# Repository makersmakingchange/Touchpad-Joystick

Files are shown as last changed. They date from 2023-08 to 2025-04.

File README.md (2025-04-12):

<!---  Open Source Assistive Technology: GitHub Readme Template  --->
<!-- Template files available at https://github.com/makersmakingchange/OpenAT-Template -->
 
<!-- TITLE -->
# Touchpad Joystick

<!-- SUMMARY -->
The Touchpad Joystick is a joystick that is activated by touch. This device is a more affordable option to many commercial joysticks and trackpads on the market. This is a USB joystick that can be plugged into either the left, or right USB joystick of the Xbox Adaptive Controller.

The Touchpad Joystick is comprised of a commercially available capacitive touch sensor (Cirque Capacitive Touch Sensor 35 mm) that is mounted in a 3d printed enclosure.

This Joystick was designed by Ron Nelson. 

<!-- PHOTO --->
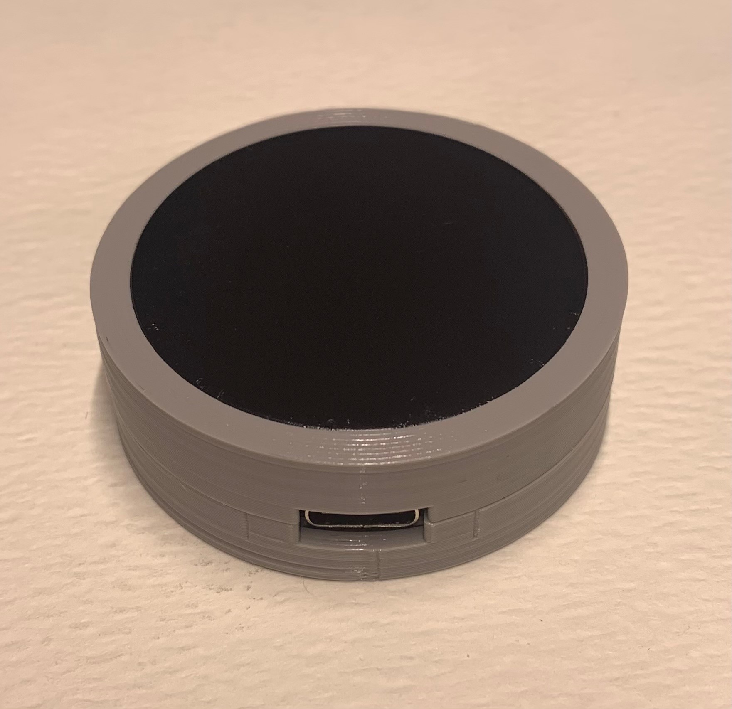
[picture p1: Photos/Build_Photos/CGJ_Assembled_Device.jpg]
Touchpad joystick with a grey case.


## Makers Making Change Assistive Device Library
 - https://www.makersmakingchange.com/s/product/touchpad-joystick/](https://www.makersmakingchange.com/s/product/touchpad-joystick/01tJR000000Be3lYAC

## Getting Started

### 1. Order the Off-The-Shelf Components
The [Bill of Materials](/Documentation/Touchpad_Joystick_BOM.csv) lists all of the parts and components required to build the Touchpad Joystick. The electronic components may be available locally, but will probably need to be ordered online. 

### 2. Print the 3D Printable components
Print the components for the switch tester case and choose an option for the case.

All of the files and individual print files can be in the [/Build_Files/3D_Printing_Files](/Build_Files/3D_Printing_Files/) folder.

### 3. Assemble the Touchpad Joystick
Reference the [assembly guide](/Documentation/Touchpad_Joystick_Assembly_Guide.pdf) for the tools and steps required to build each portion.

## Files
<!--- FILES --->

### Documentation
<!--- DOCUMENTATION --->
| Document | Version | Link |
|----------|---------|------|
| Design Rationale     | 1.0 | [Touchpad_Joystick_Design_Rationale](/Documentation/Touchpad_Joystick_Design_Rationale.pdf) |
| Bill of Materials    | 1.0 | [Touchpad_Joystick_BOM](/Documentation/Touchpad_Joystick_BOM.csv) |
| Assembly Guide       | 1.0 | [Touchpad_Joystick_Assembly_Guide](/Documentation/Touchpad_Joystick_Assembly_Guide.pdf) |
| Maker Checklist      | 1.0 | [Touchpad_Joystick_Checklist](/Documentation/Touchpad_Joystick_Maker_Checklist.pdf) |
| User Quick Guide     | 1.0 | [Touchpad_Joystick_User_Quick_Guide](/Documentation/Touchpad_Joystick_User_Guide.pdf)           |
| Changelog            | 1.0 | [Touchpad_Joystick_Changelog](/Documentation/Touchpad_Joystick_Changelog.pdf)               |

### Build Files
<!--- BUILD FILES --->
 - [3D Printing Files](/Build_Files/3D_Printing_Files)

## License
<!--- LICENSE --->
Everything needed or used to design, make, test, or prepare the Touchpad Joystick is licensed under the CERN 2.0 Weakly Reciprocal license <https://ohwr.org/project/cernohl/wikis/Documents/CERN-OHL-version-2> (CERN-OHL-W).

All software is under the GNU General Public License v3.0 (GPL-3.0). 

Accompanying material such as instruction manuals, videos, and other copyrightable works that are useful but not necessary to design, make, test, or prepare the Touchpad Joystick are published under a Creative Commons Attribution-ShareAlike 4.0 license <https://creativecommons.org/licenses/by-sa/4.0/> (CC BY-SA 4.0).

## Attribution
<!--- ATTRIBUTION --->
 - The original design was created by [Ron Nelson](https://github.com/nelsonii) under an [MIT License](https://github.com/nelsonii/JoystickEnclosures/blob/main/LICENSE)
 - Documentation by Neil Squire Society / Makers making Change
 - The documentation template was created by [Neil Squire](https://www.neilsquire.ca/) / [Makers Making Change](https://makersmakingchange.com/) and is used under a CC BY-SA 4.0 license. It is available at the following link: https://github.com/makersmakingchange/OpenAT-Template

----

<!-- ABOUT MMC START -->
## About Makers Making Change
[Makers Making Change Logo](https://www.makersmakingchange.com/)

Makers Making Change is a program of [Neil Squire](https://www.neilsquire.ca/), a Canadian non-profit that uses technology, knowledge, and passion to empower people with disabilities.

Makers Making Change leverages the capacity of community based Makers, Disability Professionals and Volunteers to develop and deliver affordable Open Source Assistive Technologies.

 - Website: [www.MakersMakingChange.com](https://www.makersmakingchange.com/)
 - GitHub: [makersmakingchange](https://github.com/makersmakingchange)
 - Bluesky: [@makersmakingchange.bsky.social](https://bsky.app/profile/makersmakingchange.bsky.social)
 - Instagram: [@makersmakingchange](https://www.instagram.com/makersmakingchange)
 - Facebook: [makersmakechange](https://www.facebook.com/makersmakechange)
 - LinkedIn: [Neil Squire Society](https://www.linkedin.com/company/neil-squire-society/)
 - Thingiverse: [makersmakingchange](https://www.thingiverse.com/makersmakingchange/about)
 - Printables: [MakersMakingChange](https://www.printables.com/@MakersMakingChange)

### Contact Us
For technical questions, to get involved, or to share your experience we encourage you to [visit our website](https://www.makersmakingchange.com/) or [contact us](https://www.makersmakingchange.com/s/contact).
<!-- ABOUT MMC END -->

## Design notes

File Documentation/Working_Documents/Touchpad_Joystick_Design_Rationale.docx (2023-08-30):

# Introduction

This device is a capacitive touchscreen joystick that allows users to connect to the XAC and operate a joystick with little to zero force. This device is well suited for users with limited dexterity and finger strength.

# Research

## Commercial Products

Title | Picture | Price | Notes

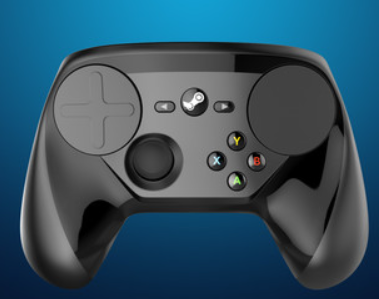
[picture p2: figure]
A photo of the Steam controller.

Steam Controller (https://store.steampowered.com/app/353370/Steam_Controller/) | | N/A | This commercial gaming controller made by Steam uses a trackpad joystick instead of the standard analog joystick. Considered a commercial flop and is no longer available.

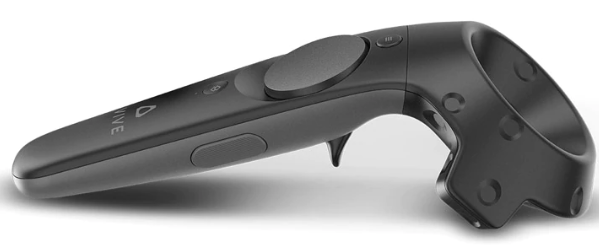
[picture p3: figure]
A photo of the Vive controller.

Vive Controller (https://www.vive.com/ca/accessory/controller/) | | $179.99 | A controller used for VR gaming that uses a track pad joystick

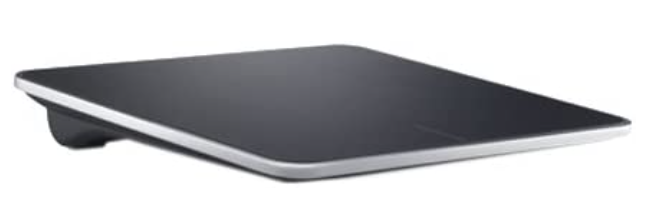
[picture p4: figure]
A photo of the Dell Wireless Touchpad.

Dell Wireless Touchpad (https://www.amazon.com/dp/B00AM0SI16/?tag=tguru-20&th=1) | | $109.99 | A wireless trackpad that can connect to a computer through a USB dongle.

## DIY Products

Title | Picture | Price | Notes

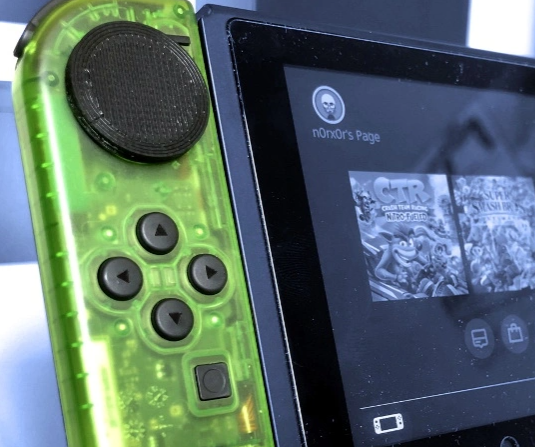
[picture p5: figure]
A photo of the Joy-Con touchpad mod.

Joy-Con Touchpad Mod (https://medium.com/@matteo.pisani.91/how-i-hacked-nintendo-joy-con-controller-8ac22d75b0b8) | | | “The initial inspiration for this project was to create a permanent solution to joystick fatigue and drifting issues” Replaces the stock joystick with the Cirque GlidePoint (https://www.cirque.com/glidepoint-circle-trackpads) capacitive joystick.

# Requirements

## Goals

G01 | Offer users an alternative to analog joysticks.
G02 | Allow users to control their joystick with little to no activation force.
G03 | Use capacitive touch to control joystick movements.

## Functional Requirements

F01 | Must be compatible with the XAC.
F02 | Must use common connection types to connect the device to the XAC.

## Non-functional Requirement

NF01 | 3D printed parts must be printable on common maker printers.
NF02 | 3D printed parts should be printable with no supports.

## Constraints

C01 | Must use readily available off the shelf parts.
C02 | Must be buildable using common maker tools.

# Version 1.0

## GlidePoint Joystick MKII

Designer: Ron Nelson

Cost: ~$32

Print Time: ~1h

GitHub Repository: nelsonii (Ron Nelson) (github.com) (https://github.com/nelsonii)

- Contains firmware and housing designs for various devices made by Ron Nelson, including the glide point joystick.

YouTube: GlidePoint as Joystick for XBOX Adaptive Controller - YouTube (https://www.youtube.com/watch?v=LsAF-lyaMcg)

- Brief explanation of the prototyping process.

Other Resources:

ATMakers - Makers & Users | Facebook (https://www.facebook.com/groups/ATMakers/) – Some discussion of device.

Cirque Glidepoint Light Touch Switch - YouTube (https://www.youtube.com/watch?v=ezXU3xq22Q4) – Review of product.

SevenMileMountain - Etsy Canada (https://www.etsy.com/shop/SevenMileMountain?) – Etsy shop where Ron Nelson currently sells mounts for this device.

### Cirque GlidePoint Sensor

The GlidePoint is a capacitive trackpad that is used as a joystick in this project. There are three sizes available: 23 mm, 35 mm, and 40 mm in diameter.

There are also 4 different top surfaces available:

1. Curved Overlay
2. Flat Overlay
3. Adhesive Overlay
4. No Overlay

### Device Configurations

Configuration | GlidePoint Variants | Microcontroller Options | Enclosure
1 (MKII) | - 35 mm - Curved Overlay (https://www.mouser.ca/ProductDetail/355-TM0350352024-003) | - QT PY SAMD21 (https://www.mouser.ca/ProductDetail/485-4600) - QT PY RP2040 (https://www.mouser.ca/ProductDetail/485-4900) | - Top (https://github.com/nelsonii/JoystickEnclosures/blob/main/CirquePoint/CirqueGlidePointMKII_Enclosure_QTPy_Top_Disc_35mmWithOverlay_v1A.stl) - Base (https://github.com/nelsonii/JoystickEnclosures/blob/main/CirquePoint/CirqueGlidePointMKII_Enclosure_QTPy_Bottom_35mmWithOverlay_v1A.stl)
2 | - 23 mm - Flat Overlay (https://www.mouser.ca/ProductDetail/Cirque/TM023023-2024-002?qs=sGAEpiMZZMu3sxpa5v1qrmePy6bg6o9mPlv2NExs3Z8%3D) - 23mm - No Overlay (https://www.mouser.ca/ProductDetail/Cirque/TM023023-2024-000?qs=sGAEpiMZZMu3sxpa5v1qrmePy6bg6o9mqjFnvRi8yK8%3D) | - QT PY SAMD21 (https://www.mouser.ca/ProductDetail/485-4600) - QT PY RP2040 (https://www.mouser.ca/ProductDetail/485-4900) | - Top (https://github.com/nelsonii/JoystickEnclosures/blob/main/CirquePoint/CirquePoint_Enclosure_QTPy_Top_Disc_23mm_QTPy_v1H.stl) - Base (https://github.com/nelsonii/JoystickEnclosures/blob/main/CirquePoint/CirquePoint_Enclosure_QTPy_Bottom_23mm_v1H.stl)
3 | - 35 mm - Flat Overlay (https://www.mouser.ca/ProductDetail/Cirque/TM035035-2024-002?qs=sGAEpiMZZMu3sxpa5v1qrmePy6bg6o9mljGtaoJl40o%3D) - 35 mm - Adhesive Overlay (https://www.mouser.ca/ProductDetail/Cirque/TM035035-2024-001) - 35 mm - No Overlay (https://www.mouser.ca/ProductDetail/Cirque/TM035035-2024-000?qs=sGAEpiMZZMu3sxpa5v1qrmePy6bg6o9mfunfVZT7bg4%3D) | - QT PY SAMD21 (https://www.mouser.ca/ProductDetail/485-4600) - QT PY RP2040 (https://www.mouser.ca/ProductDetail/485-4900) | - Top (https://github.com/nelsonii/JoystickEnclosures/blob/main/CirquePoint/CirquePoint_Enclosure_QTPy_Top_Disc_35mm_QTPy_v1H.stl) - Base (https://github.com/nelsonii/JoystickEnclosures/blob/main/CirquePoint/CirquePoint_Enclosure_QTPy_Bottom_35mm_v1H.stl)
4 | - 40 mm - Flat Overlay (https://www.mouser.ca/ProductDetail/Cirque/TM040040-2024-302) - 40 mm - Adhesive Overlay (https://www.mouser.ca/ProductDetail/Cirque/TM040040-2024-300?qs=sGAEpiMZZMu3sxpa5v1qrmePy6bg6o9mo1FSrB0r8pw%3D) - 40 mm - No Overlay (https://www.mouser.ca/ProductDetail/Cirque/TM040040-2024-301?qs=sGAEpiMZZMu3sxpa5v1qrmePy6bg6o9mSWgtNQf0SXM%3D) | - QT PY SAMD21 (https://www.mouser.ca/ProductDetail/485-4600) - QT PY RP2040 (https://www.mouser.ca/ProductDetail/485-4900) | - Top NA or uses other top. - Base (https://github.com/nelsonii/JoystickEnclosures/blob/main/CirquePoint/CirquePoint_Enclosure_QYPy_Bottom_40mm_v1C.stl)
5 | - 35 mm - Flat Overlay (https://www.mouser.ca/ProductDetail/Cirque/TM035035-2024-002?qs=sGAEpiMZZMu3sxpa5v1qrmePy6bg6o9mljGtaoJl40o%3D) - 35 mm - Adhesive Overlay (https://www.mouser.ca/ProductDetail/Cirque/TM035035-2024-000?qs=sGAEpiMZZMu3sxpa5v1qrmePy6bg6o9mfunfVZT7bg4%3D) - 35 mm - No Overlay (https://www.mouser.ca/ProductDetail/Cirque/TM035035-2024-000?qs=sGAEpiMZZMu3sxpa5v1qrmePy6bg6o9mfunfVZT7bg4%3D) | - KB2040 – RP2040 (https://www.mouser.ca/ProductDetail/Adafruit/5302?qs=Rp5uXu7WBW%252B5BBDEK5EDhw%3D%3D) | - Top (https://github.com/nelsonii/JoystickEnclosures/blob/main/CirquePoint/CirquePoint_Enclosure_KB2040_Top_Disc_35mm_v1C.stl) - Base (https://github.com/nelsonii/JoystickEnclosures/blob/main/CirquePoint/CirquePoint_Enclosure_KB2040_Bottom_35or40mm_v1C.stl)
6 | - 40 mm - Flat Overlay (https://www.mouser.ca/ProductDetail/Cirque/TM040040-2024-302) - 40 mm - Adhesive Overlay (https://www.mouser.ca/ProductDetail/Cirque/TM040040-2024-300?qs=sGAEpiMZZMu3sxpa5v1qrmePy6bg6o9mo1FSrB0r8pw%3D) - 40 mm - No Overlay (https://www.mouser.ca/ProductDetail/Cirque/TM040040-2024-301?qs=sGAEpiMZZMu3sxpa5v1qrmePy6bg6o9mSWgtNQf0SXM%3D) | - KB2040 – RP2040 (https://www.mouser.ca/ProductDetail/Adafruit/5302?qs=Rp5uXu7WBW%252B5BBDEK5EDhw%3D%3D) | - Top (https://github.com/nelsonii/JoystickEnclosures/blob/main/CirquePoint/CirquePoint_Enclosure_KB2040_Top_Disc_40mm_v1C.stl) - Base (https://github.com/nelsonii/JoystickEnclosures/blob/main/CirquePoint/CirquePoint_Enclosure_KB2040_Bottom_35or40mm_v1C.stl)

### License

MIT License

Copyright (c) 2022 Ron Nelson

Permission is hereby granted, free of charge, to any person obtaining a copy of this software and associated documentation files (the "Software"), to deal in the Software without restriction, including without limitation the rights to use, copy, modify, merge, publish, distribute, sublicense, and/or sell copies of the Software, and to permit persons to whom the Software is furnished to do so, subject to the following conditions:

The above copyright notice and this permission notice shall be included in all copies or substantial portions of the Software.

THE SOFTWARE IS PROVIDED "AS IS", WITHOUT WARRANTY OF ANY KIND, EXPRESS OR IMPLIED, INCLUDING BUT NOT LIMITED TO THE WARRANTIES OF MERCHANTABILITY, FITNESS FOR A PARTICULAR PURPOSE AND NONINFRINGEMENT. IN NO EVENT SHALL THE AUTHORS OR COPYRIGHT HOLDERS BE LIABLE FOR ANY CLAIM, DAMAGES OR OTHER LIABILITY, WHETHER IN AN ACTION OF CONTRACT, TORT OR OTHERWISE, ARISING FROM, OUT OF OR IN CONNECTION WITH THE SOFTWARE OR THE USE OR OTHER DEALINGS IN THE SOFTWARE.

# Testing

## 3D Printing

Device printing successfully without the need of support. The top and bottom of the enclosure fit together nicely.

## Assembly

Wires could be shorter to fit better or note the gauge of wire to be smaller.

## Functional Test

### Connecting to XAC

Plugging in the joystick to the left or right USB input on the XAC and testing on Gamepad-Tester is successful.

Current testing

- Soldered components
  - Soldered easily.
  - Should have used less stiff wire as this made it more difficult to install components into the enclosure.
- Uploaded code
  - Had to download Adafruit board backage
  - Downloaded Neopixel and TinyUSB libraries
  - Forgot to change “Optimize:” to “Faster” as defined in the code.

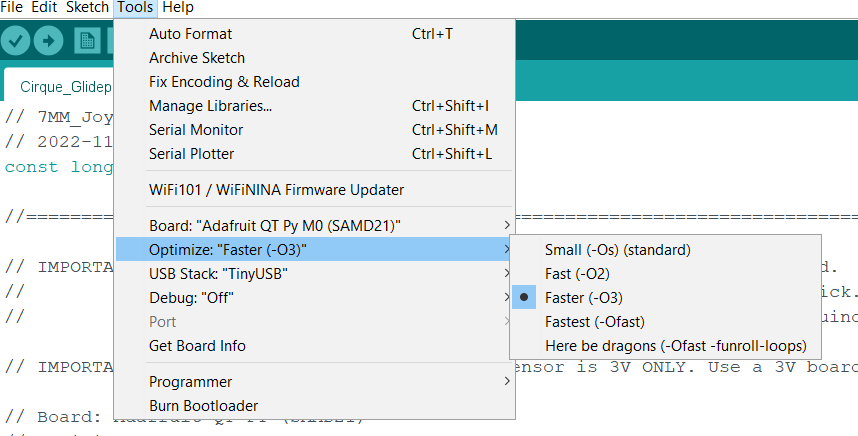
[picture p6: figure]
A screenshot of the Arduino IDE Tools menu optimization options.

# Opportunities for Improvement

- Create a 3D printed handheld mount.
- Have markers to establish joystick orientation.
- Have the enclosure halves click-lock together.

© 2023 by Neil Squire Society This work is licensed under the CC BY SA 4.0 License: http://creativecommons.org/licenses/by-sa/4.0 Files available at https://github.com/makersmakingchange/Touchpad-Joystick Page 1 of 1

V1.0 | August 2023 Touchpad Joystick Design Rationale

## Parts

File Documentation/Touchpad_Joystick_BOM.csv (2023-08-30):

Touchpad Joystick |  |  |  |  |  |  |  | Unit Cost | Total Cost | Total Print time (hr) | Total filament (g)
Version: V1.0 |  | Last Updated: August 8, 2023 |  |  |  |  |  | $32.00 | $32.00 | 1.00 | 7
Commercial Parts
ID | Part Name | Part Type | QTY | QTY/PKG | $/PKG | PKG QTY | $/Unit | Extended | Total | Link
TM035035-2024-003 | Cirque Capacitive Touch Sensor 35 mm | Electrical | 1 | 1 | $12.14 | 1 | $12.14 | $12.14 | $12.14 | https://www.mouser.ca/ProductDetail/355-TM0350352024-003
4600 | Adafruit QT PY - SAMD21 | Microcontroller | 1 | 1 | $10.35 | 1 | $10.35 | $10.35 | $10.35 | https://www.mouser.ca/ProductDetail/485-4600
SC-2CAK010M | USB Cable (C Male / A Male) | Electrical | 1 | 1 | $9.33 | 1 | $9.33 | $9.33 | $9.33 | https://www.mouser.ca/ProductDetail/530-SC-2CAK010M
 |  |  |  |  |  | 0 | $- | $- | $-
 |  |  |  |  |  | 0 | $- | $- | $-
 |  |  |  |  |  | 0 | $- | $- | $-
 |  |  |  |  |  | 0 | $- | $- | $-
3D Printed Parts ESTIMATED PRICING USING 1KG ROLL COST: |  | $25.00
ID | Part | Material | QTY | Mass (g) / Unit | Time / Unit |  | Print Time (Min) | Estimated Price |  | Link
 | Enclosure Top | PLA | 1 | 2 | 20 |  | 20 | $0.05
 | Enclosure Bottom | PLA | 1 | 5 | 40 |  | 40 | $0.13
 |  |  |  |  |  |  |  | $-
 |  |  |  |  |  |  |  | $-
 |  |  |  |  |  |  |  | $-
 |  |  |  |  |  |  |  | $-
Custom Printed Circuit Board (PCB)
ID | Part |  | QTY
Tools for Assembly
 | 3D Printer
 | Soldering Iron
 | Solder
 | Wire Strippers
 | Flush Cutters
Alternatives (if there are other sources for some parts link them below)
ID | Part and description |  |  |  |  |  |  |  |  | Link

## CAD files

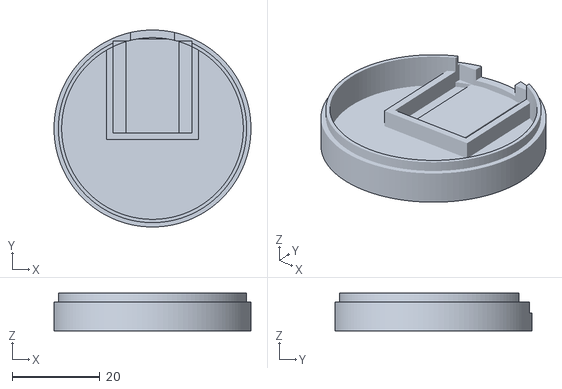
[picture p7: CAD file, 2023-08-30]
Build_Files/3D_Printing_Files/Joystick_Enclosure_Bottom_35.stl
45.0 x 45.0 x 8.65

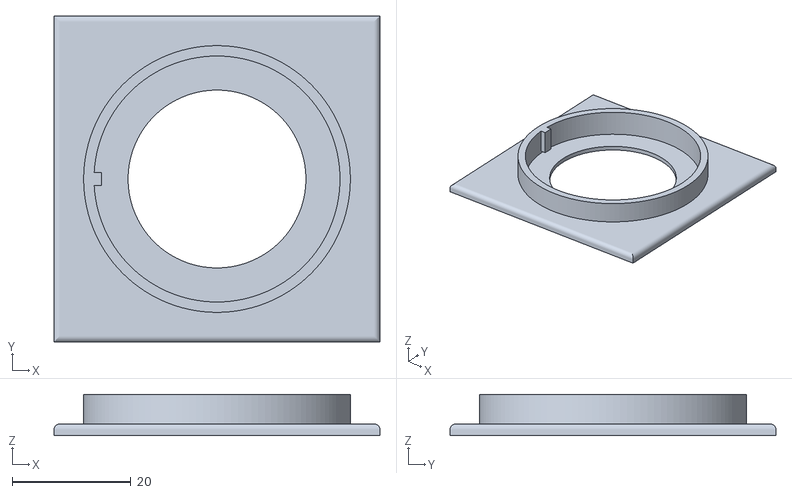
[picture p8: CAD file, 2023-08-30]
Build_Files/3D_Printing_Files/Soldering_Jig_35_(Optional).stl
55.0 x 55.0 x 7.00

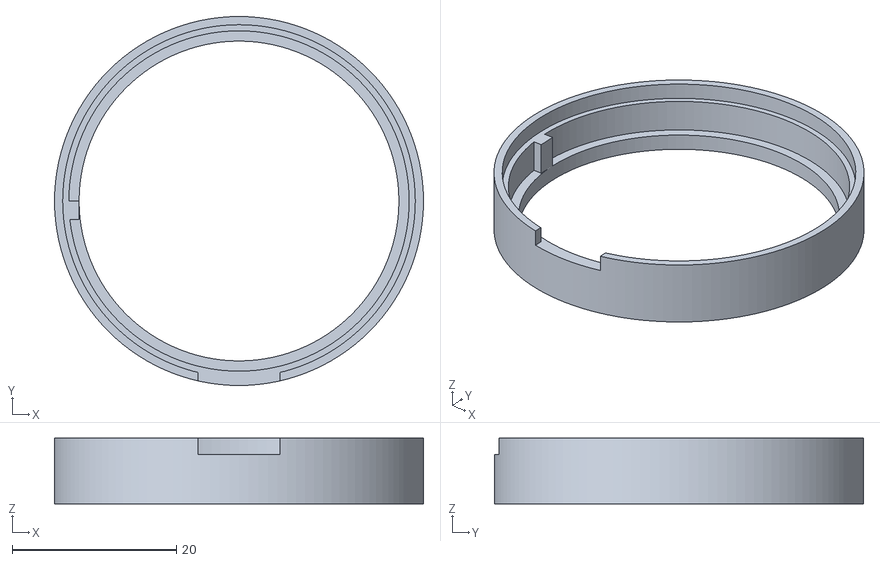
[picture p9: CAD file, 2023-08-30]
Build_Files/3D_Printing_Files/Joystick_Enclosure_Top_35.stl
45.0 x 45.0 x 8.00

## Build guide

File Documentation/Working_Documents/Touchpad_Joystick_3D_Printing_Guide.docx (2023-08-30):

# 3D Printing Summary

Configuration | Total Print Time (min) | Total Number of Components | Typical Total Mass (g) | Typical Number of Print Setups
Joystick Enclosure | 60 | 2 | 7 | 1

# 3D Printing Settings

Print File Name | Qty | Total Print Time (hr:min) | Mass (g) | Infill (%) | Support (Y/N) | Layer Height/ Nozzle Diameter(mm) | Notes (orientation, special settings, etc.)
Joystick_Enclosure_Bottom_35.stl | 1 | 0:40 | 5 | 20 | N | 0.2/0.4 | Print in given orientation.
Joystick_Enclosure_Top.stl | 1 | 0:20 | 2 | 20 | N | 0.2/0.4 | Print in given orientation.

# Customization Options

Users may request their choice of print colour.

# Post-Processing

Inspect that all parts are smooth, and edges are non-sharp. Use sandpaper as necessary.

# Examples of Quality Prints

Photos of Enclosure Top

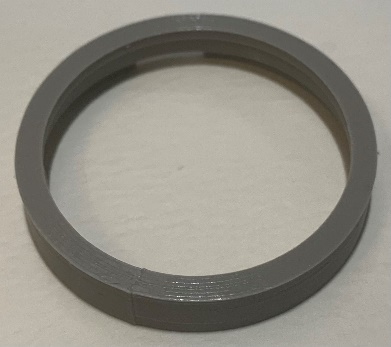
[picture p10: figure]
A photo of the exterior of the top enclosure piece printed in black PLA.
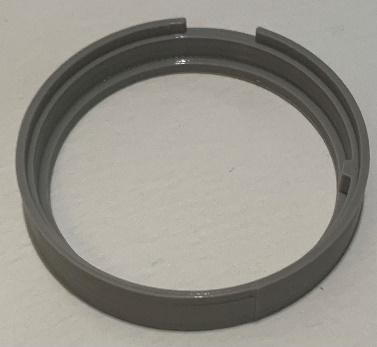
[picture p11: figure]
A photo of the interior of the top enclosure piece printed in black PLA.

Photos of Enclosure Bottom

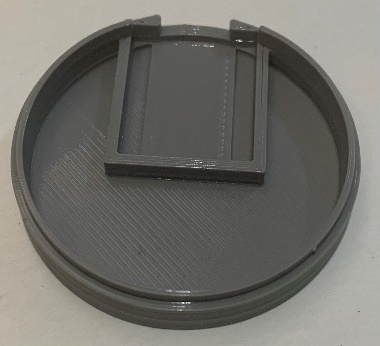
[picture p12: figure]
A photo of the interior of the bottom enclosure piece printed in black PLA.
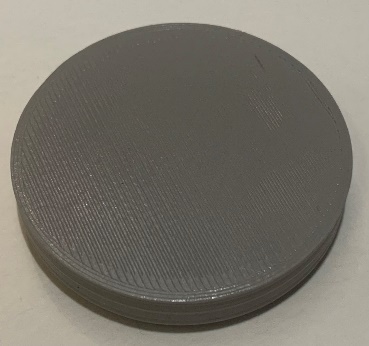
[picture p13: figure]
A photo of the exterior of the bottom enclosure piece printed in black PLA.

© 2023 by Neil Squire This work is licensed under the CC BY SA 4.0 License: http://creativecommons.org/licenses/by-sa/4.0 Files available at https://github.com/makersmakingchange/Touchpad-Joystick Page 1 of 2

V1.0 | August 2023 Trackpad Joystick 3D Printing Guide

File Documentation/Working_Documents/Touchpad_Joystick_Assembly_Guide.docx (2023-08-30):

# Required Components

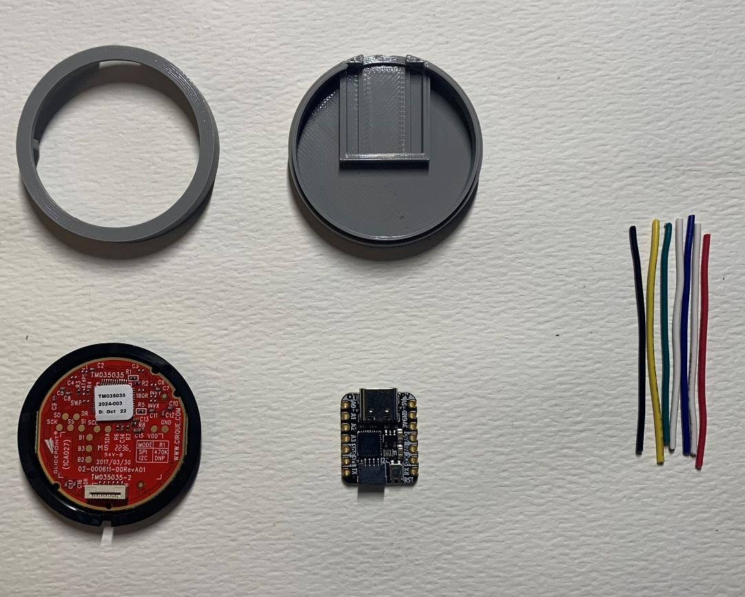
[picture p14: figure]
A photo of the components required to build the Touchpad Joystick.

5. 4. 3. 2. 1.A | BOM 1. Enclosure Base 2. Enclosure Top 3. Cirque Capacitive Sensor 4. QT PY Micro Controller 5. 5cm long 22AWG wire x7

# Required Tools

- Soldering Iron
- Solder
- Wire Strippers
- Flush Cutter
- Glue

# Required Personal Protective Equipment (PPE)

- Safety Glasses
- Fume Extractor or a well-ventilated space

# Assembly Instructions

## Step 1: Prepare Wires

Cut seven lengths of wire approximately 5 cm long and strip approximately 1cm off each end.

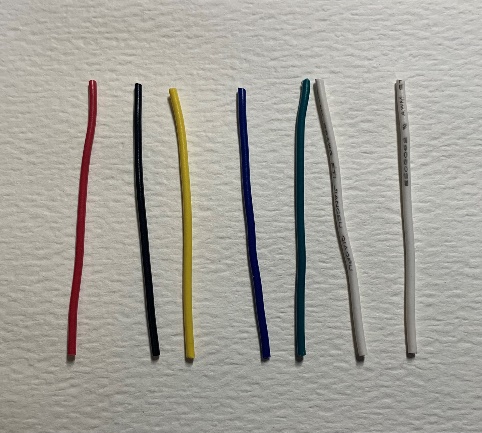
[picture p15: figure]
A photo of seven pieces of wire cut to five centimeters.
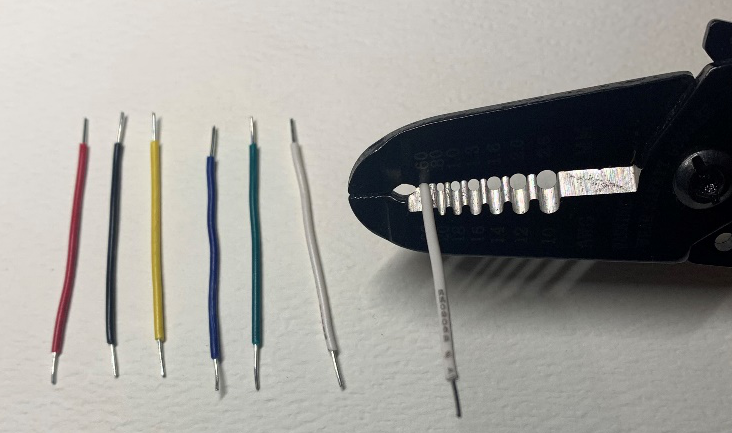
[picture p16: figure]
A photo of stripping the wires for the device build.

## Step 2: Solder the Capacitive Sensor Connections

Solder each wire to one of the contacts on the back of the capacitive sensor as specified in the table and image below. Ensure the wires and solder only touches their specified contact point and does not bridge to any others. Snip any excess wire.

Wire # | Contact Label on Sensor
1 | DR
2 | S0
3 | SCK
4 | SS
5 | SI
6 | VDD
7 | GND

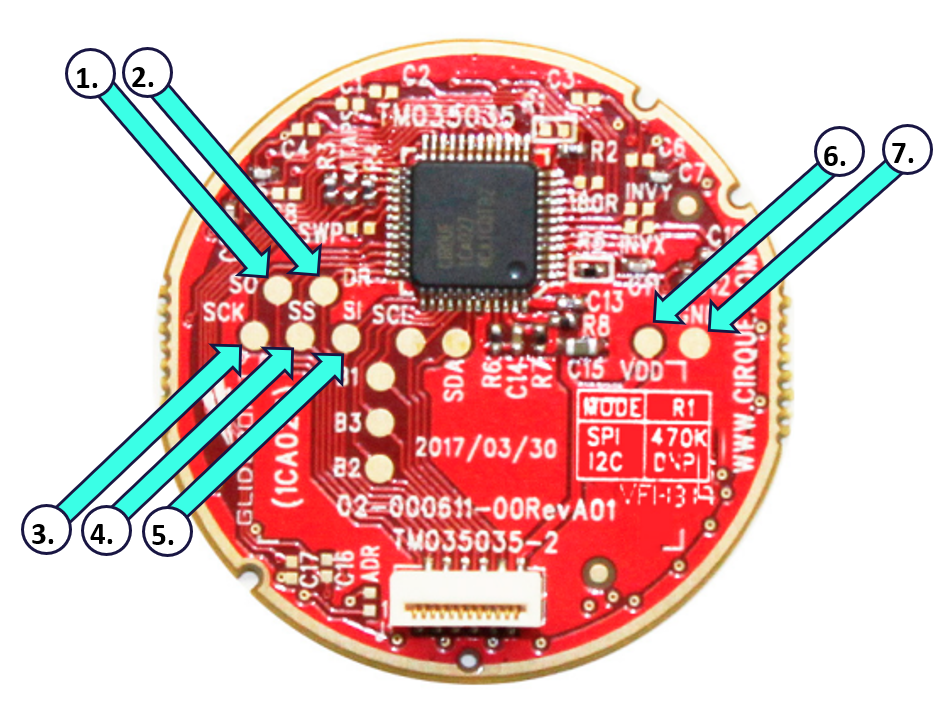
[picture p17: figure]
An image of the Cirque Glidepoint circuit board with arrows pointing to each soldering contact.
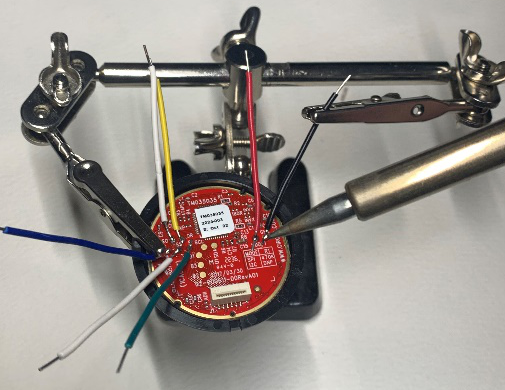
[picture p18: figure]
A photo of the wires soldered to the Cirque Glidepoint circuit board.

2.

1.

1.

1.

## Step 3: Solder the Controller Connections

Take note of the wire numbers from Step 2 and solder them to the controller pins as specified in the table and images below. When soldering, feed the wires though the top of the controller and snip the excess from the bottom once secure.

Wire # | Pin on Controller
1 | A1
2 | MI
3 | SCK
4 | A0
5 | MO
6 | 3V
7 | GND

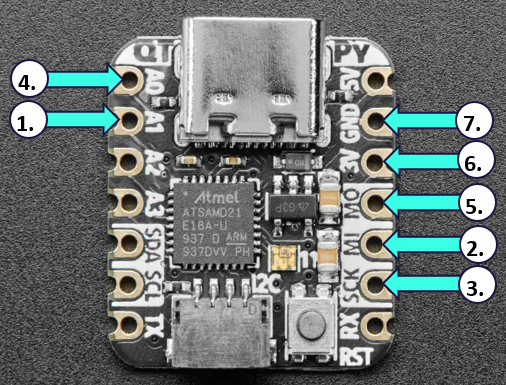
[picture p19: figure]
A photo of the microcontroller with arrows pointing to each required pin.
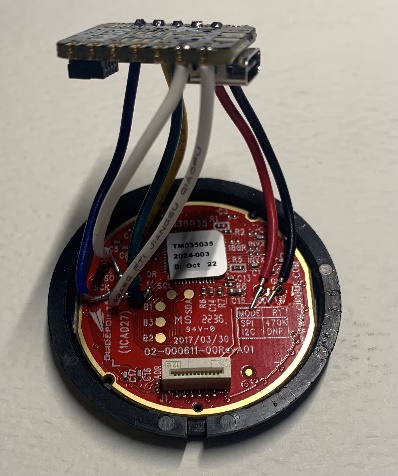
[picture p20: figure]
A photo of the wires soldered to both the Cirque Glidepoint cirquit board and the microcontroller.

## Step 4: Install into Enclosure

Press the controller into the enclosure base, making sure to align the USB port with the cut-out on the side. Then press the sensor into the enclosure top by alighting their outer notches. The two halves of the enclosure can now be pressed together and secured with a dab of glue.

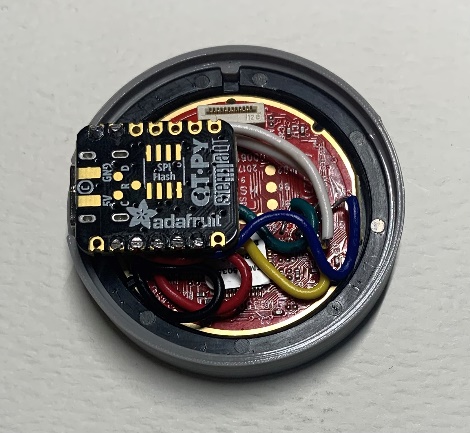
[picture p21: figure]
A photo of the Cirque Glidepoint board mounted in the 3D printed top.
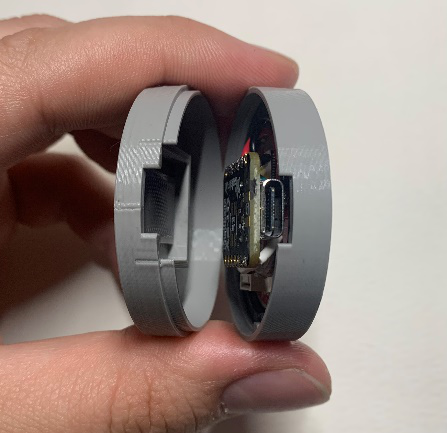
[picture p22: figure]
A photo of the enclosure being assembled.
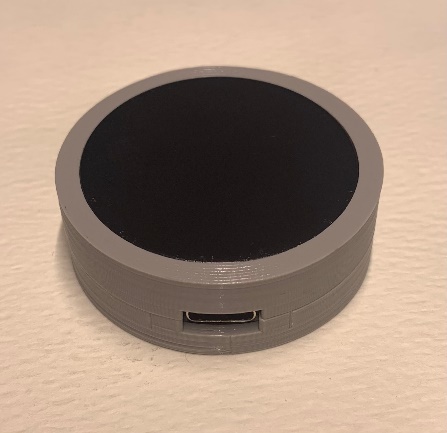
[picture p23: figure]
A photo of the completed Touchpad Joystick.

# Firmware Instructions

## Step 1: Download Firmware

The latest version of the firmware can be found in the GitHub repository (https://github.com/nelsonii/JoystickSoftware/tree/main/7MM_Joystick_GlidePoint_MKII). Save the file with a “.ino” extension at the end of the file name.

## Step 2: Download / Open Arduino IDE

Download and install the latest version of the Arduino IDE: https://www.arduino.cc/en/software

## Step 3: Set Board

With the Arduino IDE open, select the Adafruit QT Py board. To do this, click on Tools → Board → Select Adafruit QT Py M0 (SAMD21)

## Step 4: Connect Device

Use the USB cable connect the device to a computer and allow a few seconds for it to initialize.

## Step 5: Open Firmware

Open the device firmware and click “OK” to create a sketch folder if prompted.

## Step 7: Install Libraries

This device requires the Adafruit_NeoPixel and Adafruit_TinyUSB libraries. To install these libraries:

Click Tools → Manage Libraries → Search “Adafruit_NeoPixel” and then “Adafruit_TinyUSB” → click Install for each one, respectively.

## Step 6: Select the Port #

The corresponding port number to the connected controller must be selected: Click Tools → Port → COM ## (this number will vary for each user).

## Step 7: Upload Code

Click the right arrow on the top left of the Arduino IDE to upload the code. Once the upload is complete, a message saying “Upload Successful” will show at the bottom left of the Arduino IDE.

## Testing using an Xbox Adaptive Controller

1. Connect the Xbox Adaptive Controller (XAC) using a USB C cable to the computer.
2. Plug the joystick into either the left or right USB joystick ports.
3. If using Windows, open “Set up USB Game Controllers” from the Control Panel. You can find this by searching your computer in the search bar next to the Windows icon.
4. Select the Xbox Adaptive Controller from the list of controllers and go to “Properties”.
5. Move your joystick by touching the trackpad and observe the movement of the cross hatch in the “Axes” window. Ensure it moves in the proper directions when you move the joystick (the USB cable exit points in the up/forward direction). If not, open the joystick and check your connections or modify the directions in the code.

Alternatively, you could use the XAC with Steam or an Xbox itself to test that moving the joystick results in the corresponding movements on the controller.

© 2023 by Neil Squire This work is licensed under the CC BY SA 4.0 License: http://creativecommons.org/licenses/by-sa/4.0 Files available at https://github.com/makersmakingchange/Touchpad-Joystick Page 1 of 1

V1.0 | August 2023 Touchpad Joystick Assembly Guide

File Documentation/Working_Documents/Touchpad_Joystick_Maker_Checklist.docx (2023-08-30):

# Maker To Do List

- Read through the Assembly Guide to become familiar with required components, tools, supplies, and safety gear and overall assembly steps.
- Talk to User about customization options (e.g., colour, any special requests, etc.)
- Order hardware components
- Gather tools, supplies, and safety equipment.
- Assemble the device
  - Flash code to the device
- Test device
- Print “User Guide”

# Items to Give to User

- Assembled, tested device
- “User Guide”

© 2023 by Neil Squire This work is licensed under the CC BY SA 4.0 License: http://creativecommons.org/licenses/by-sa/4.0 Files available at https://github.com/makersmakingchange/Touchpad-Joystick Page 1 of 1

V1.0 | August 2023 Touchpad Joystick Maker Checklist

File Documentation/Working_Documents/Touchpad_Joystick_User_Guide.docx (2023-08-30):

## Introduction

The Touchpad Joystick is a small USB Cirque Glidepoint touchpad that functions as a gaming joystick. The activation surface is 35mm in diameter and is touch sensitive. It plugs into USB and can be used to play games with the Xbox Adaptive Controller

## Features

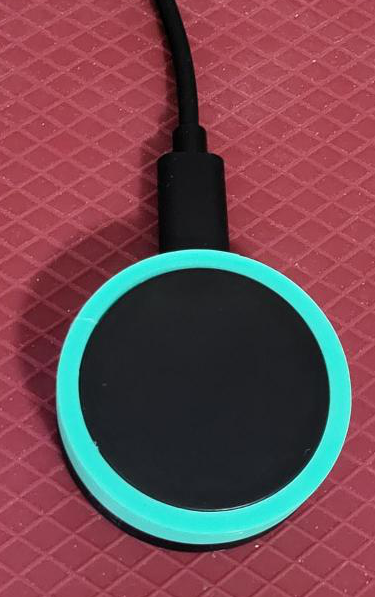
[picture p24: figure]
A photo of the Touchpad Joystick with arrows pointing to its features.

Forward Direction

Cirque Glidepoint Trackpad

USB Cable

## Usage

To use this joystick, simply plug the USB cable into the host device. The forward direction is where the USB cable exits the joystick itself. The joystick is touch sensitive and the joystick speed is proportional to the distance your finger is from the centre of the touchpad. Removing your finger from the touchpad will return the joystick to neutral.

## Compatibility

This joystick is compatible with the XAC and with PC. To add buttons, you can use 3rd party software such as Joystick Gremlin (https://github.com/WhiteMagic/JoystickGremlin) to combine switch inputs or keyboard keys with the joystick into a virtual gamepad.

## Specifications

Diameter | 45 mm
Height | 16 mm
Diameter of Activation Surface | 35 mm
Weight | 30 grams

## Cleaning

Use a damp cloth to wipe down the surface of the device. Do not use hot water as this may cause the 3D printed components to warp. Do not submerge the device in any liquid. (Water, disinfectant, etc.)

© 2023 by Neil Squire This work is licensed under the CC BY SA 4.0 License: http://creativecommons.org/licenses/by-sa/4.0 Files available at https://github.com/makersmakingchange/Touchpad-Joystick Page 2 of 3

V1.0 | August 2023 Touchpad Joystick user Quick Guide

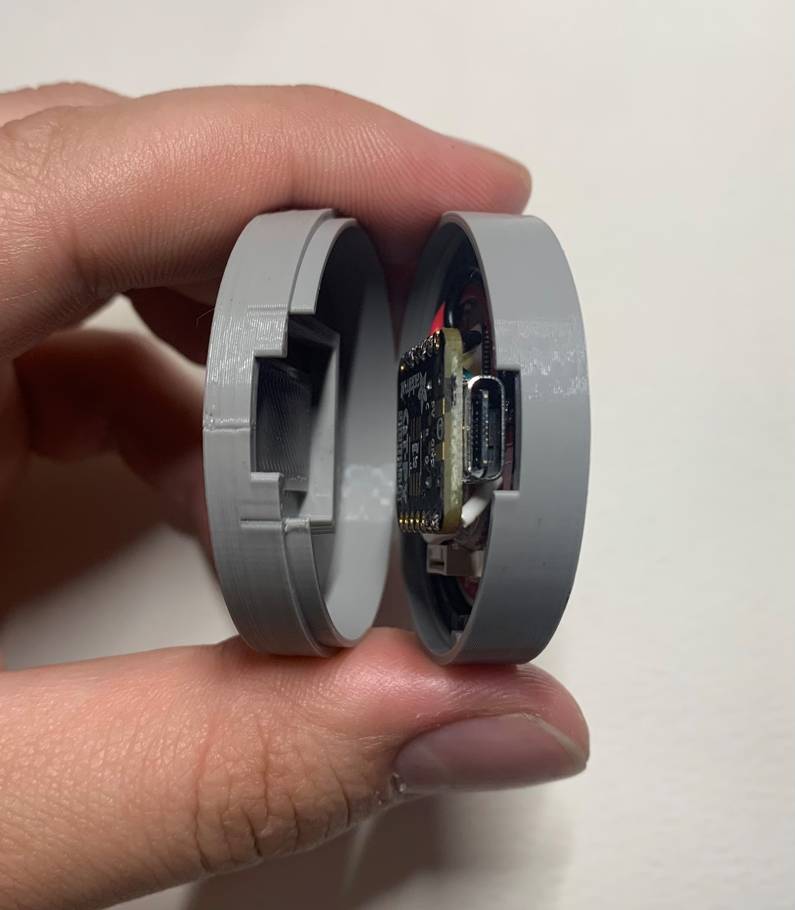
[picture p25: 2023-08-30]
Photos/Build_Photos/CGJ_Enclosure_Alignment.jpg

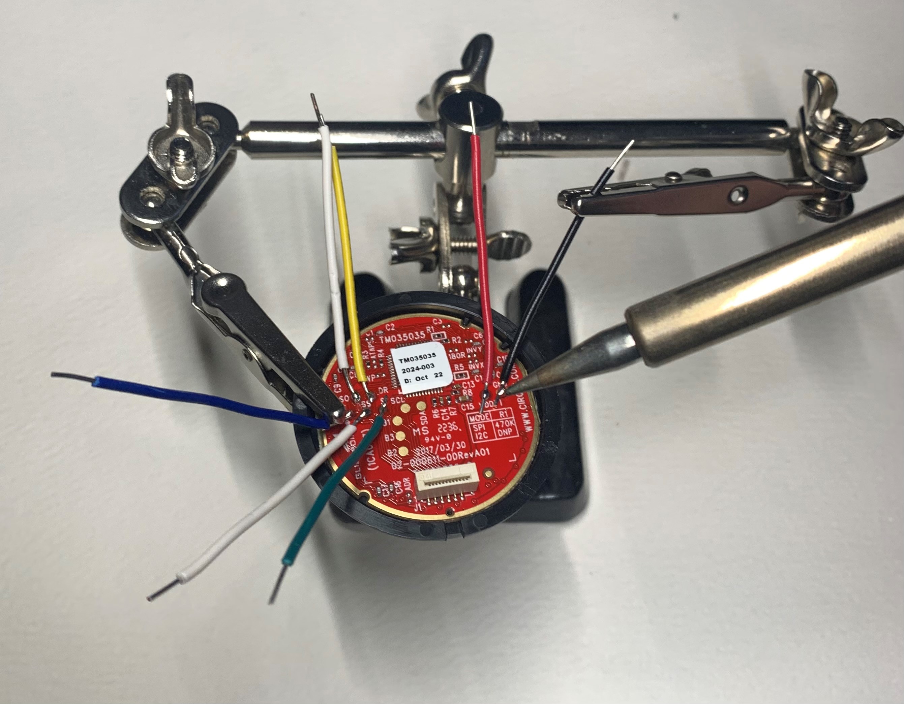
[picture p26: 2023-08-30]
Photos/Build_Photos/CGJ_Sensor_Soldering.jpg

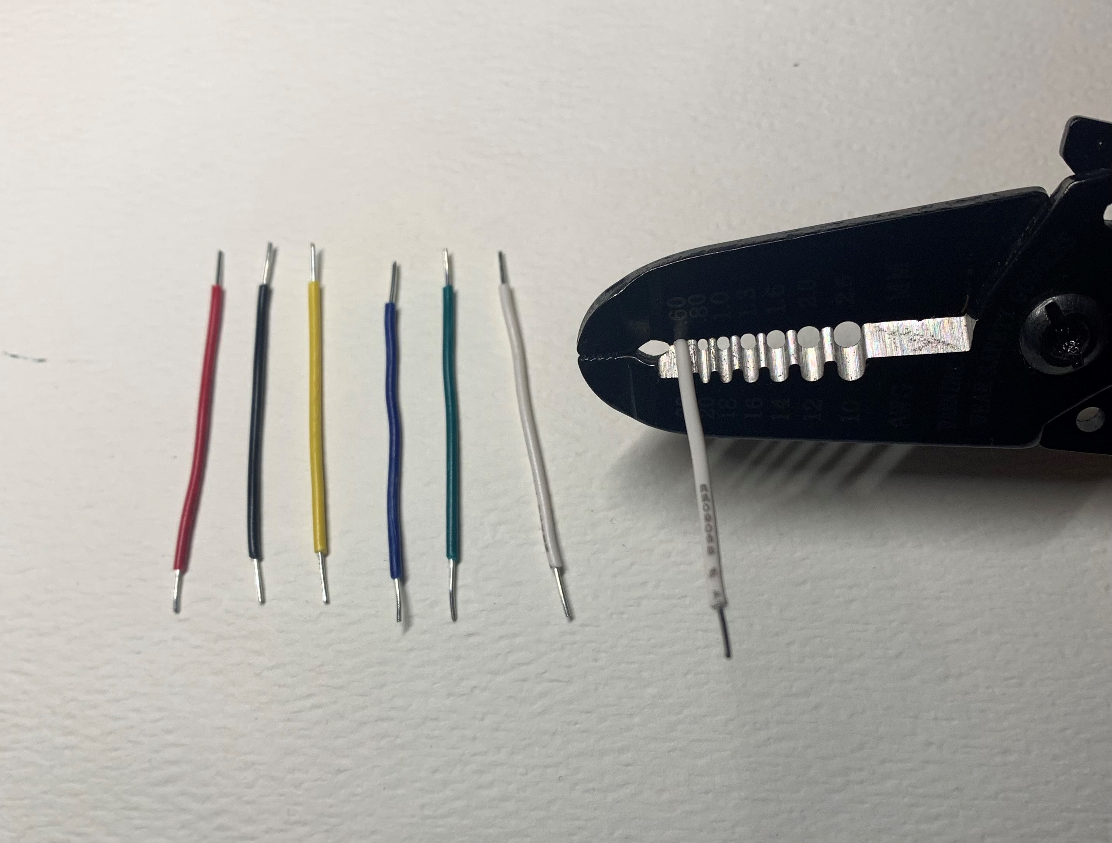
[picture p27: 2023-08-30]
Photos/Build_Photos/CGJ_Wire_Stripping.jpg

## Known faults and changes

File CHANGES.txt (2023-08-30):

Version 1.0 | Date 2023-Aug-30
•	Ron Nelson's joystick deisgn curated within the Touchpad Joystick repository
•	Documentation by Neil Squire Society uploaded to Touchpad Joystick repository

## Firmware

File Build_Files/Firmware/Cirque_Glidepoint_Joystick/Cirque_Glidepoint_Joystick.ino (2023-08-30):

// 7MM_Joystick_GlidePoint_MKII_v1A
// 2022-11-14-A
const long buildDate = 2022111401;

//=================================================================================

// IMPORTANT: For the GlidePoint device I am using the QT PY (SAMD21) board.
//            You MUST use the TinyUSB package instead of the usual "joystick.h".
//                TOOLS >> USB STACK >> TinyUSB must be selected (not "arduino").

// IMPORTANT: The Cirque/Pinnacle/GlidePoint sensor is 3V ONLY. Use a 3V board!!!

// Board: Adafruit QT PY (SAMD21)
// Optimize: Faster (-O3)
// USB Stack: TinyUSB  <-- Important: Using TinyUSB, not Arduino USB!
// Debug: Off
// Port: COMxx (Adafruit QT PY (SAMD21))

// This sketch is only valid on boards which have native USB support
// and compatibility with Adafruit TinyUSB library. 
// For example SAMD21, SAMD51, nRF52840.


//=================================================================================
// MIT License
// Copyright (c) 2022 Ron Nelson

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
//=================================================================================

const boolean debug = true; // if true, output info to serial monitor or plotter.

//=================================================================================

#include <SPI.h>
#include <Adafruit_NeoPixel.h>
#include <Adafruit_TinyUSB.h>

//=================================================================================

Adafruit_NeoPixel pixels = Adafruit_NeoPixel(1, PIN_NEOPIXEL);

uint32_t red = pixels.Color(255,0,0);
uint32_t green = pixels.Color(0,255,0);
uint32_t blue = pixels.Color(0,0,255);
uint32_t black = pixels.Color(0,0,0);

//=================================================================================

//Joystick via TinyUSB
uint8_t const desc_hid_report[] = { TUD_HID_REPORT_DESC_GAMEPAD() };
Adafruit_USBD_HID usb_hid(desc_hid_report, sizeof(desc_hid_report), HID_ITF_PROTOCOL_NONE, 2, false);
hid_gamepad_report_t    joystick;

//=================================================================================

// CIRQUE: Hardware pin-number labels
#define CS_PIN    0 // A0
#define DR_PIN    1 // A1

// CIRQUE: Masks for Cirque Register Access Protocol (RAP)
#define WRITE_MASK  0x80
#define READ_MASK   0xA0

// CIRQUE: Register config values
#define SYSCONFIG_1   0x00
#define FEEDCONFIG_1  0x03
#define FEEDCONFIG_2  0x1F
#define Z_IDLE_COUNT  0x05

// CIRQUE: Coordinate scaling values
#define PINNACLE_XMAX     2047    // max value Pinnacle can report for X
#define PINNACLE_YMAX     1535    // max value Pinnacle can report for Y
#define PINNACLE_X_LOWER  127     // min "reachable" X value
#define PINNACLE_X_UPPER  1919    // max "reachable" X value
#define PINNACLE_Y_LOWER  63      // min "reachable" Y value
#define PINNACLE_Y_UPPER  1471    // max "reachable" Y value
#define PINNACLE_X_RANGE  (PINNACLE_X_UPPER-PINNACLE_X_LOWER)
#define PINNACLE_Y_RANGE  (PINNACLE_Y_UPPER-PINNACLE_Y_LOWER)
#define ZONESCALE 256   // divisor for reducing x,y values to an array index for the LUT
#define ROWS_Y ((PINNACLE_YMAX + 1) / ZONESCALE)
#define COLS_X ((PINNACLE_XMAX + 1) / ZONESCALE)

// CIRQUE: ADC-attenuation settings (held in BIT_7 and BIT_6)
// 1X = most sensitive, 4X = least sensitive
#define ADC_ATTENUATE_1X   0x00
#define ADC_ATTENUATE_2X   0x40
#define ADC_ATTENUATE_3X   0x80
#define ADC_ATTENUATE_4X   0xC0

#define ADC_LOWER_DEFAULT  0x02

// CIRQUE: Select the overlay type
// 1 = Curved Overlay, 0 = Flat Overlay
#define SENSE0_OVERLAY_CURVE  1


typedef struct _absData
{
  uint16_t xValue;
  uint16_t yValue;
  uint16_t zValue;
  uint8_t buttonFlags;
  bool touchDown;
  bool hovering;
} absData_t;

absData_t touchData;


// These values require tuning for optimal touch-response
// Each element represents the Z-value below which is considered "hovering" in that XY region of the sensor.
// The values present are not guaranteed to work for all HW configurations.
const uint8_t ZVALUE_MAP[ROWS_Y][COLS_X] =
{
  {0, 0,  0,  0,  0,  0, 0, 0},
  {0, 2,  3,  5,  5,  3, 2, 0},
  {0, 3,  5, 15, 15,  5, 2, 0},
  {0, 3,  5, 15, 15,  5, 3, 0},
  {0, 2,  3,  5,  5,  3, 2, 0},
  {0, 0,  0,  0,  0,  0, 0, 0},
};

//=================================================================================

int joyMin = -127;
int joyMax = +127;

int rawHorz, rawVert; // raw values from sensor
int lmtHorz, lmtVert; // limited (range checked) value
int mapHorz, mapVert; // mapped value (limited)

// invert if needed
bool invHorz = true; 
bool invVert = true; 

// set the default min/max values. determined during testing.
int minHorz=50; // was: 100
int maxHorz=1000; // was: 900
int minVert=50;
int maxVert=1000;

//=================================================================================

void setup() {
  
  if (debug) { Serial.begin(115200); }

  pinMode(CS_PIN, OUTPUT);
  pinMode(DR_PIN, INPUT);

  // Startup the NeoPixel
  pixels.begin(); pixels.clear(); pixels.setPixelColor(0, red); pixels.show();
  
  // Startup SPI and TrackPoint
  SPI.begin();
  Pinnacle_Init();

  // These functions are required for use with thick overlays (curved)
  setAdcAttenuation(ADC_ATTENUATE_2X);
  tuneEdgeSensitivity();

  #if defined(ARDUINO_ARCH_MBED) && defined(ARDUINO_ARCH_RP2040)
    // Manual begin() is required on core without built-in support for TinyUSB such as mbed rp2040
    TinyUSB_Device_Init(0);
  #endif

  // Startup the joystick
  // IMPORTANT: This will loop until device is mounted.
  //            So, if you see a RED light, it's powered, but not mounted.
  //            When the LED goes GREEN, it's mounted.
  //            When touched (sending data) LED goes BLUE
  usb_hid.begin();
  while( !TinyUSBDevice.mounted() ) delay(10);

  Pinnacle_EnableFeed(true);

}

//=================================================================================

void loop() {
  
  if(DR_Asserted())
  {    
    
    Pinnacle_GetAbsolute(&touchData); // Get the data from the GlidePoint
    Pinnacle_CheckValidTouch(&touchData);     // Checks for "hover" caused by curved overlays
    ScaleData(&touchData, 1024, 1024);  // Scale coordinates to X, Y resolution

    rawHorz = (int) touchData.xValue;
    rawVert = (int) touchData.yValue;

    lmtHorz = rawHorz;
    lmtVert = rawVert;
    if (lmtHorz<minHorz) {lmtHorz=minHorz;}
    if (lmtHorz>maxHorz) {lmtHorz=maxHorz;}
    if (lmtVert<minVert) {lmtVert=minVert;}
    if (lmtVert>maxVert) {lmtVert=maxVert;}
    

    // Map values to a range the XAC likes
    mapHorz = map(lmtHorz, minHorz, maxHorz, joyMin, joyMax);
    mapVert = map(lmtVert, minVert, maxVert, joyMin, joyMax);

    if (debug) {
      Serial.print("Build: ");
      Serial.print(buildDate);      
      Serial.print(" T: ");
      Serial.print(touchData.touchDown);
      Serial.print(" X: ");
      Serial.print(touchData.xValue);
      Serial.print(" Y: ");
      Serial.print(touchData.yValue);
      Serial.print(" Z: ");
      Serial.print(touchData.zValue);
      Serial.print(" RH: ");
      Serial.print(rawHorz);
      Serial.print(" RV: ");
      Serial.print(rawVert);
      Serial.print(" LH: ");
      Serial.print(lmtHorz);
      Serial.print(" LV: ");
      Serial.print(lmtVert);
      Serial.print(" MH: ");
      Serial.print(mapHorz);
      Serial.print(" MV: ");
      Serial.print(mapVert);
      Serial.println();
    }

    if ( usb_hid.ready() ) {
      joystick.x = mapHorz;
      joystick.y = mapVert;
      usb_hid.sendReport(0, &joystick, sizeof(joystick));
    }
  
  }//DR_Asserted

  if (touchData.touchDown) {
    pixels.clear(); pixels.setPixelColor(0, blue); pixels.show();
  }
  else { 
    pixels.clear(); pixels.setPixelColor(0, green); pixels.show(); 
    if ( usb_hid.ready() ) { joystick.x = 0; joystick.y = 0; usb_hid.sendReport(0, &joystick, sizeof(joystick)); }
  }

}//loop

//=================================================================================



/*  Pinnacle-based TM040040 Functions  */

void Pinnacle_Init()
{
  DeAssert_CS();

  // Host clears SW_CC flag
  Pinnacle_ClearFlags();
  // Host configures bits of registers 0x03 and 0x05
  RAP_Write(0x03, SYSCONFIG_1);
  RAP_Write(0x05, FEEDCONFIG_2);
  // Host enables preferred output mode (absolute)
  RAP_Write(0x04, FEEDCONFIG_1);
  // Host sets z-idle packet count to 5 (default is 30)
  RAP_Write(0x0A, Z_IDLE_COUNT);
}

void Pinnacle_GetAbsolute(absData_t * result)
{
// Reads XYZ data from Pinnacle registers 0x14 through 0x17
// Stores result in absData_t struct with xValue, yValue, and zValue members

  uint8_t data[6] = { 0,0,0,0,0,0 };
  RAP_ReadBytes(0x12, data, 6);
  Pinnacle_ClearFlags();

  result->buttonFlags = data[0] & 0x3F;
  result->xValue = data[2] | ((data[4] & 0x0F) << 8);
  result->yValue = data[3] | ((data[4] & 0xF0) << 4);
  result->zValue = data[5] & 0x3F;
  result->touchDown = result->xValue != 0;
}

void Pinnacle_ClearFlags()
{
  // Clears Status1 register flags (SW_CC and SW_DR)
  RAP_Write(0x02, 0x00);
  delayMicroseconds(50);
}


void Pinnacle_EnableFeed(bool feedEnable)
{
  // Enables/Disables the feed
  uint8_t temp;
  RAP_ReadBytes(0x04, &temp, 1);  // Store contents of FeedConfig1 register
  if(feedEnable)
  {
    temp |= 0x01;                 // Set Feed Enable bit
    RAP_Write(0x04, temp);
  }
  else
  {
    temp &= ~0x01;                // Clear Feed Enable bit
    RAP_Write(0x04, temp);
  }
}

//=================================================================================

/*  Curved Overlay Functions  */
// Adjusts the feedback in the ADC, effectively attenuating the finger signal
// By default, the the signal is maximally attenuated (ADC_ATTENUATE_4X for use with thin, flat overlays
void setAdcAttenuation(uint8_t adcGain)
{
  uint8_t temp = 0x00;

  if (debug) { Serial.println(); }
  if (debug) { Serial.println("Setting ADC gain..."); }
  ERA_ReadBytes(0x0187, &temp, 1);
  temp &= 0x3F; // clear top two bits
  temp |= adcGain;
  ERA_WriteByte(0x0187, temp);
  ERA_ReadBytes(0x0187, &temp, 1);
  if (debug) { Serial.print("ADC gain set to:\t"); }
  if (debug) { Serial.print(temp &= 0xC0, HEX); }
  switch(temp)
  {
    case ADC_ATTENUATE_1X:
      if (debug) { Serial.println(" (X/1)"); }
      break;
    case ADC_ATTENUATE_2X:
      if (debug) { Serial.println(" (X/2)"); }
      break;
    case ADC_ATTENUATE_3X:
      if (debug) { Serial.println(" (X/3)"); }
      break;
    case ADC_ATTENUATE_4X:
      if (debug) { Serial.println(" (X/4)"); }
      break;
    default:
      break;
  }
}

// Changes thresholds to improve detection of fingers
void tuneEdgeSensitivity()
{
  uint8_t temp = 0x00;

  if (debug) { Serial.println(); }
  if (debug) { Serial.println("Setting xAxis.WideZMin..."); }
  ERA_ReadBytes(0x0149, &temp, 1);
  if (debug) { Serial.print("Current value:\t"); }
  if (debug) { Serial.println(temp, HEX); }
  ERA_WriteByte(0x0149,  0x04);
  ERA_ReadBytes(0x0149, &temp, 1);
  if (debug) { Serial.print("New value:\t"); }
  if (debug) { Serial.println(temp, HEX); }

  if (debug) { Serial.println(); }
  if (debug) { Serial.println("Setting yAxis.WideZMin..."); }
  ERA_ReadBytes(0x0168, &temp, 1);
  if (debug) { Serial.print("Current value:\t"); }
  if (debug) { Serial.println(temp, HEX); }
  ERA_WriteByte(0x0168,  0x03);
  ERA_ReadBytes(0x0168, &temp, 1);
  if (debug) { Serial.print("New value:\t"); }
  if (debug) { Serial.println(temp, HEX); }
}
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
